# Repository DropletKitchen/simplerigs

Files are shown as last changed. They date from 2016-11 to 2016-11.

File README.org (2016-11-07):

* Simple Microfluidics Rigs with Inexpensive Board Cameras

*This page describes how to build an optics rig based on board cameras
for droplet microfluidics.*

This is a [[https://DropletKitchen.github.io][DropletKitchen]] project.

If not stated otherwise, the designs and documentation in this repository
is Copyright (c) 2016 Martin Fischlechner and DropletKitchen Contributors,
and made available under a
[[https://creativecommons.org/licenses/by/4.0/][Creative Commons Attribution 4.0 International (CC BY 4.0)]] License.

#+CAPTION: Image of the rig at several stages of the build. A] fully assembled rig. The inset shows the LED with inexpensive focusing optics. B] image of the openSCAD model used to design the first version. Use this model as a starting point for your own designs. C] setup without the x,y,z-stage. The inset shows the board camera with the flipped objective removed. D] x,y,z-stage.
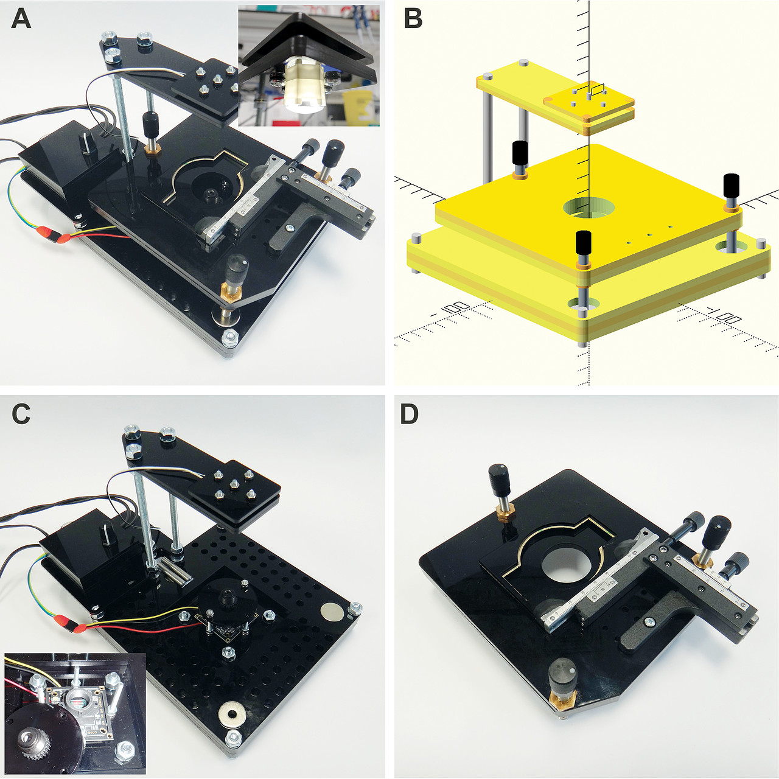
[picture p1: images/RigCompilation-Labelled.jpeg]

#+BEGIN_QUOTE
Image of the rig at several stages of the build. A] fully assembled
rig. The inset shows the LED with inexpensive focusing optics. B]
image of the openSCAD model used to design the first version. Use this
model as a starting point for your own designs. C] setup without the
x,y,z-stage. The inset shows the board camera with the flipped
objective removed. D] x,y,z-stage.
#+END_QUOTE

** Introduction
Many droplet microfluidic experiments have simple imaging
requirements, for example as a real-time quality control to ensure
droplet generation is running smoothly. This page shows how to build
simple microscopes with inexpensive board cameras. Flipping the
objective of the camera transforms the setup to a small
microscope. Magnification of the system is dependent on the distance
between the objective and the CCD or CMOS chip of the camera. In
contrast to scientific cameras, inexpensive consumer electronics
cameras or board cameras do not offer much control. They usually
self-regulate exposure times depending on the light available and
without frame rate adjustment, binning, or camera-triggering is
possible. BUT - they are incredibly cheap and often offer surprising
performance. Here we use a PS3 Eye camera and a CCD-camera that
outputs analog PAL video used for First Person View (FPV) drone
flying. While the PS3 eye is a rolling shutter camera, the board CCD
camera is global shutter, which is well suited for imaging fast
events.

#+CAPTION: This image compilation shows the performance of both cameras for observing a simple microfluidic droplet generator. The PS3Eye camera shows distortion effects due to its rolling shutter, but still allows to estimate droplet monodispersity (by virtue of width) up to velocities of 400 mm/s. The Sony CCD global shutter board camera lacks distortions, and yields useful images at higher velocities. With global shutter cameras the lightsource can additionally be strobed to enhance image quality. Due to the different chip sensor-objective distances of the setups used (see image below), the images of the PS3Eye have higher magnification. In its 'fast mode', the PS3Eye has a resolution of 320x240 (up to 180 fps) and is connected via USB. The Emax Sony 811 outputs analog video (PAL, 25fps) with a resolution of 976x582 pixels. Video can be displayed directly on a monitor. To use the camera with a computer, a framegrabber is needed.
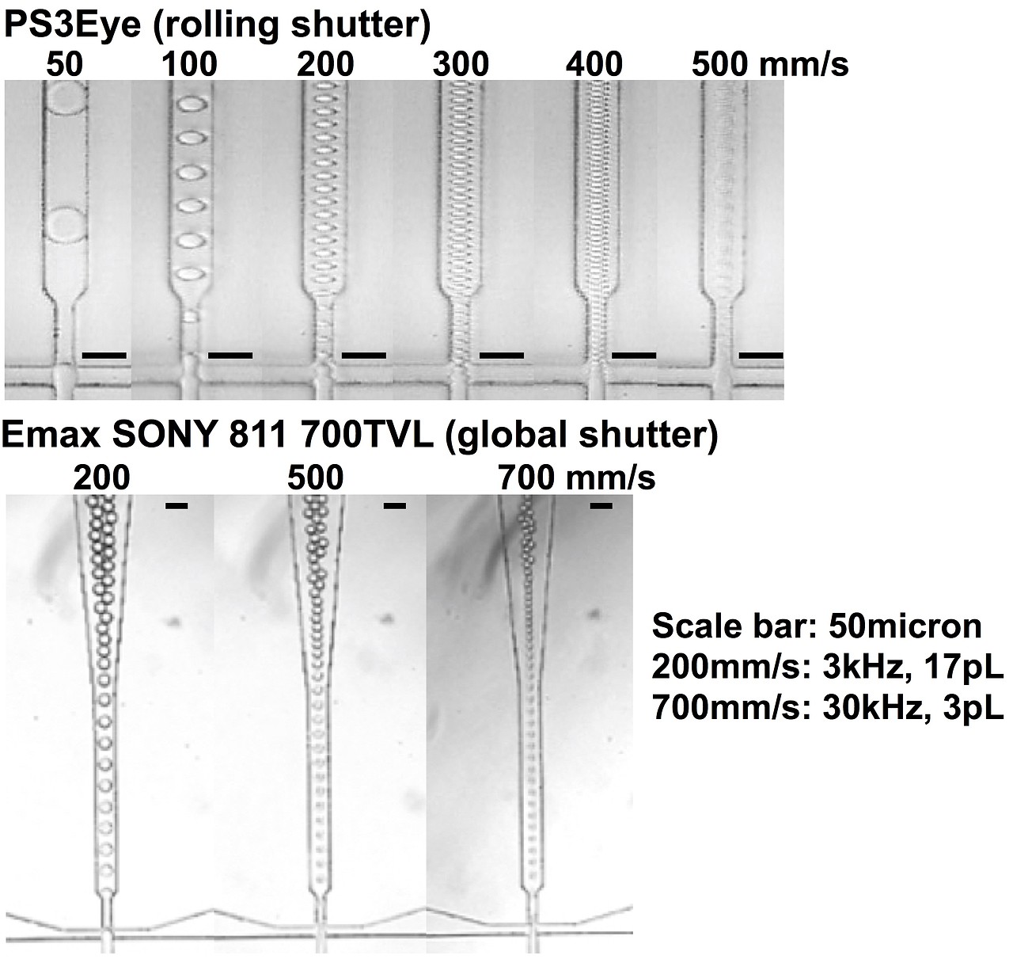
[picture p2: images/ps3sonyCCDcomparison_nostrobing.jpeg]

#+BEGIN_QUOTE
This image compilation shows the performance of both cameras for
observing a simple microfluidic droplet generator. The PS3Eye camera
shows distortion effects due to its rolling shutter, but still allows
to estimate droplet monodispersity (by virtue of width) up to
velocities of 400 mm/s. The Sony CCD global shutter board camera lacks
distortions, and yields useful images at higher velocities. With
global shutter cameras the lightsource can additionally be strobed to
enhance image quality. Due to the different chip sensor-objective
distances of the setups used (see image below), the images of the
PS3Eye have higher magnification. In its 'fast mode', the PS3Eye has a
resolution of 320x240 (up to 180 fps) and is connected via USB. The
Emax Sony 811 outputs analog video (PAL, 25fps) with a resolution of
976x582 pixels. Video can be displayed directly on a monitor. To use
the camera with a computer, a framegrabber is needed.
#+END_QUOTE

** Design
The model was first developed in openSCAD (http://www.openscad.org/)
and sliced for lasercutting
([[./files/RigSonyCCDPS3eyeBoardCameraOpenSCAD.scad]]). Later modifications
were done in a .dxf-file ([[./files/RigSonyCCDPS3eyeBoardCamera.dxf]]) with
Draftsight
(http://www.3ds.com/products-services/draftsight-cad-software/free-download/).
Starting with a 3D-model is helpful to play with overall dimensions
and shapes, but the design is quicker to modify in 2D-CAD at later
stages.

#+CAPTION: Parts for laser cutting.
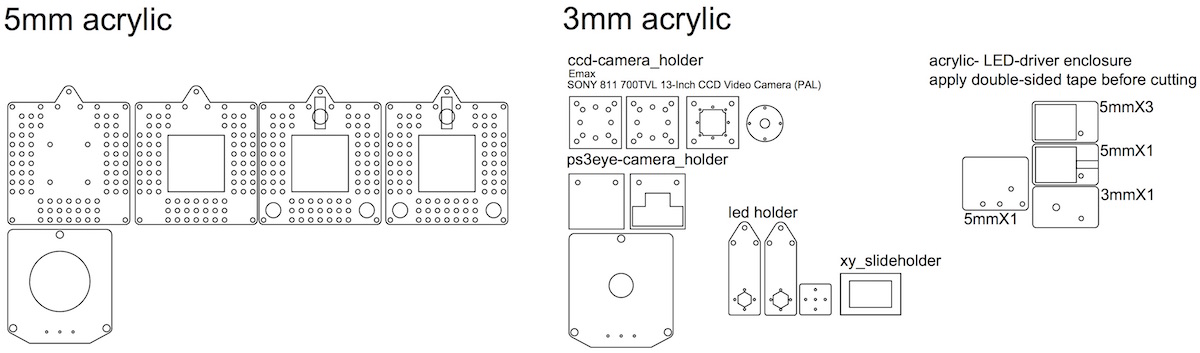
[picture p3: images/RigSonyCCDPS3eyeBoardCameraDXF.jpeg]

#+BEGIN_QUOTE
Parts for laser cutting.
#+END_QUOTE
** Materials

| Item                                                                   |      number | bought from                | part number    | approx cost (£) |
|------------------------------------------------------------------------+-------------+----------------------------+----------------+-----------------|
| Structural components                                                  |             |                            |                |                 |
|------------------------------------------------------------------------+-------------+----------------------------+----------------+-----------------|
| M6 Hex Screws (different lengths, eg l=16,20,25,30mm for flexibility)  |        many | RS or other hardware shop  |                |              NA |
| M6 Nuts, Washers, 'shake-proof washers'                                |        many | RS or other hardware shop  |                |              NA |
| M6 Threaded Rods                                                       | 3x (~150mm) | hardware shop              |                |              NA |
| M3 Screws, Nuts and Washers (different lengths)                        |        many | RS or other hardware shop  |                |              NA |
| 3mm Acrylic Sheet (410x280mm)                                          | 1 pack of 5 | www.techsoft.co.uk         | TAAC3-R3-5-COL |              18 |
| 5mm Acrylic Sheet (410x280mm)                                          | 1 pack of 5 | www.techsoft.co.uk         | TAAC3-R5-5-COL |              25 |
| Double-Sided Tape (3M, 468MP or 467MP), optional but nice to have      |           1 | RS                         | 842-1089       |              50 |
|------------------------------------------------------------------------+-------------+----------------------------+----------------+-----------------|
| XYZ-stage                                                              |             |                            |                |                 |
|------------------------------------------------------------------------+-------------+----------------------------+----------------+-----------------|
| Fine Adjustment Screw with Knob, 1/4"-80, 2.00" Long                   |           3 | Thorlabs                   | FAS200         |              17 |
| Locking Phosphor-Bronze Bushing with Nut, 1/4"-80, L=0.50"             |           3 | Thorlabs                   | N80L6P         |              21 |
| XY-stage from eBay (search 'microscope stage')                         |           1 | eBay                       |                |          max 20 |
| Eclipse 20mm Threaded Hole Neodymium Ring Magnet                       |           1 | RS                         | 792-4565       |               7 |
| Eclipse 20mm Neodymium Disc Magnet (3each, we use 5 for assembly)      |           2 | RS                         | 695-0184       |              22 |
| Short Steel Rods (magnetic) 20-40mm long, 5-6mm in diameter            |           2 | NA                         | NA             |              NA |
|------------------------------------------------------------------------+-------------+----------------------------+----------------+-----------------|
| Light                                                                  |             |                            |                |                 |
|------------------------------------------------------------------------+-------------+----------------------------+----------------+-----------------|
| RECOM POWER RCD-24-0.70/W/X3 LED Driver Adjustable                     |           1 | Farnell                    | 1793223        |              13 |
| OPULENT  REBEL-STAR-ES-NW200  High Brightness LED                      |           1 | Farnell                    | 2110405        |               4 |
| Polymer Optics 141/180, Lens Assembly                                  |           1 | RS                         | 665-6573       |               3 |
| Stripboard, 10kOhm Potentiometer                                       |             | eg Farnell, RS or other    |                |              NA |
| Male/Female 0.1" PCB Connectors                                        |             | eg Farnell, RS or other    |                |              NA |
| Sugru for isolation of wire connections...                             |           1 | cpc Farnell                | MK00041        |               6 |
| Epoxy Glue                                                             |          NA |                            | NA             |              NA |
|------------------------------------------------------------------------+-------------+----------------------------+----------------+-----------------|
| Optics/Cameras                                                         |             |                            |                |                 |
|------------------------------------------------------------------------+-------------+----------------------------+----------------+-----------------|
| Sony Playstation 3 Eye Camera (=rolling shutter)                       |           1 | amazon.co.uk               |                |              ~7 |
| Emax SONY 811 700TVL 1/3-Inch CCD Video Camera (=global shutter)       |           1 | www.unmannedtechshop.co.uk | CC7-E5A-55E    |              19 |
|------------------------------------------------------------------------+-------------+----------------------------+----------------+-----------------|

** Assembly
*** Optics
- disassemble the PS3 eye camera, you will have to remove some plastic
  on the objective (glued) to be able to flip it. The SonyCCD
  camera can be used as is, just remove the objective.

- attach the flipped objective to the camera in a way that no light
  can enter from the sides. This can either be done by clamping or
  glueing (see image below). If you want to improve magnification,
  enlarge the distance between camera-chip and objective by using a
  3D-printed tube or stack of acrylic rings. In this design
  adapter-plates were used that allow cameras to be easily exchanged. On the
  other hand they can also be just attached with some Sugru or hot
  melt glue.

#+CAPTION: Left: Playstation3 Eye camera with inverted optics. Magnification is controlled via the length of a 3D-printed tube. Right: Sony CCD board camera with inverted optics mounted with a sheet of acrylic.
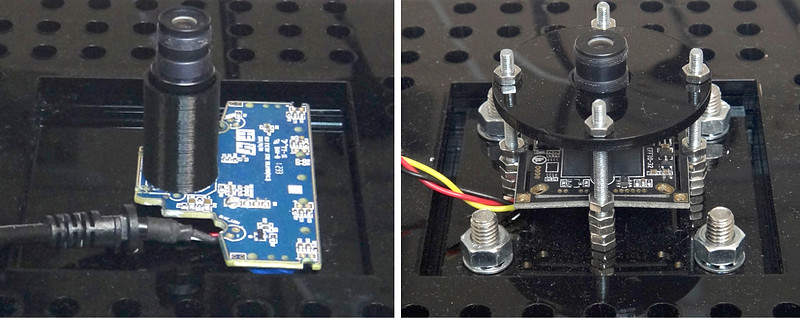
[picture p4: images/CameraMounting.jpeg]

#+BEGIN_QUOTE
Left: Playstation3 Eye camera with inverted optics. Magnification is
controlled via the length of a 3D-printed tube. Right: Sony CCD board
camera with inverted optics mounted with a sheet of acrylic.
#+END_QUOTE

*** Structure
Assembling the rig is straightforward; have a look at the image
above. Make sure that your components fit - if you change the design,
just measure components with a caliper and use exactly those
dimensions for holes etc. Laser cut parts usually results in a tight
fit. The camera with the inverted objective is held in place by
clamping it with acrylic sheets and M3 screws.

The stage is mounted on three optics screws with spherical ends in a
kinematic fashion - which defines the position of the stage by resting
on 6 points of contact. This is ideally 3 points on one, 2 on the
next, and one on the third. Here strong magnets are used to fix the
stage on its support - a ring magnet on the first side (a small cheat
but works well), 2 stacked disk magnets that magnetize two small steel
rods on top, and a stack of three disk magnets on the third point.
This assembly allows you not only to control z distance (focus), but
you can also tilt the stage and therefore have some movement in
x,y. For convenience, adding an inexpensive x,y stage is
recommended. They all differ a bit, so make sure you adapt the files
accordingly.

*** Light
For the lightsource, a star-shaped white high power LED is used which
is controlled by an adjustable LED driver. A M3 screw is used as a
heat sink and also holds the LED in place. The LED driver, a
potentiometer used to control brightness and an on/off switch is
soldered onto stripboard and then packaged in an acrylic enclosure. It
does not have to bear a lot of load, so the enclosure is based on cut
acrylic slides with double-sided tape added on one side before
cutting. This allows the structural components to be bonded together.
To focus the light of the LED onto the chip, inexpensive plastic
lenses are used. For assembly, just use a dab of epoxy glue. Do not
use 'Superglue', as cyanoacrylate vapours render optics components
cloudy over time.  Change the distance between LED and the stage such
that the image on the camera is overexposed when the LED is fully on
and the camera is set automatically to the smallest exposure time
possible. This allows you to get the best possible images of
fast-moving objects with your setup. Below is the circuit diagram for
wiring if you use the Recom LED-driver. If you want an on/off switch,
just wire it to the voltage or ground wire. Almost any power supply
will do (>=1A, 5-36V).

#+CAPTION: Circuit diagram for the Recom LED driver.
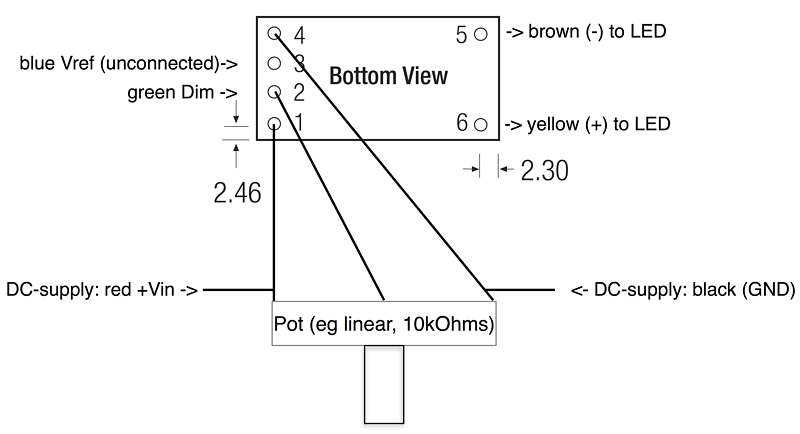
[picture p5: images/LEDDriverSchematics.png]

#+BEGIN_QUOTE
Circuit diagram for the Recom LED driver.
#+END_QUOTE

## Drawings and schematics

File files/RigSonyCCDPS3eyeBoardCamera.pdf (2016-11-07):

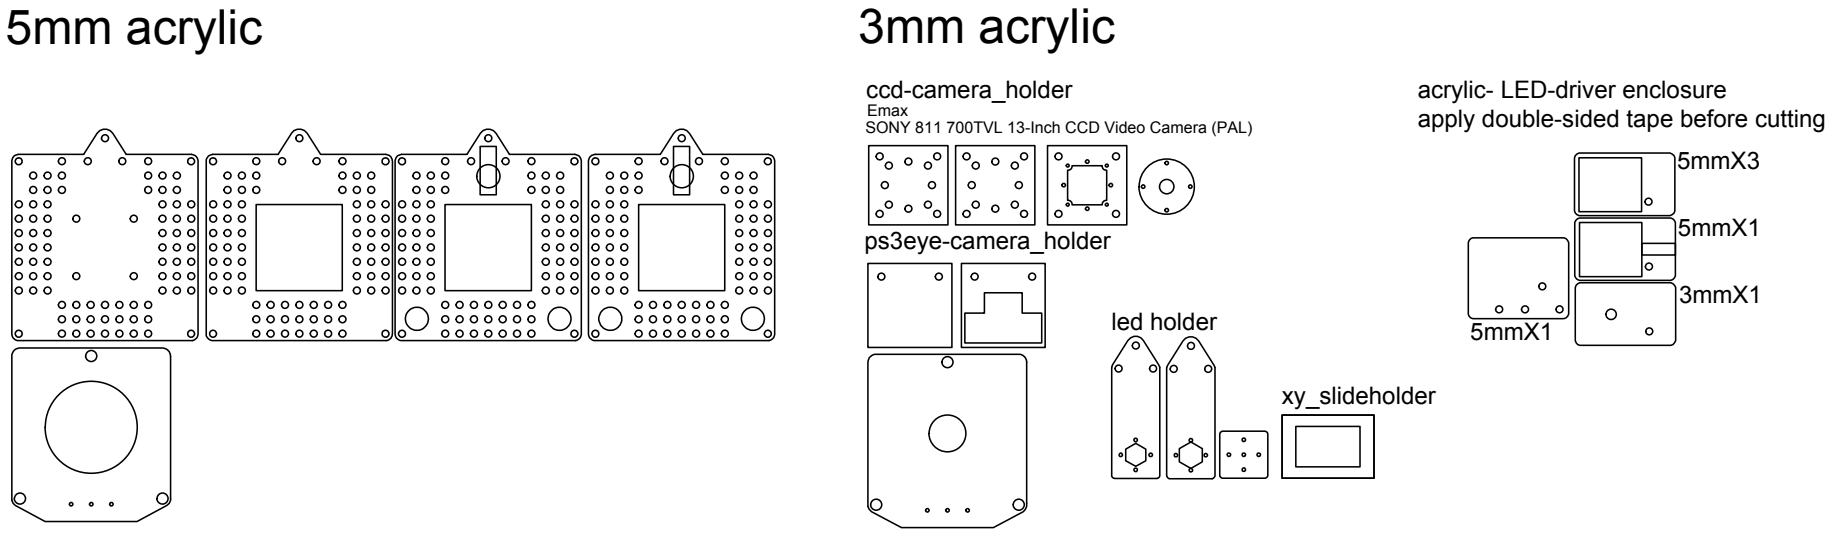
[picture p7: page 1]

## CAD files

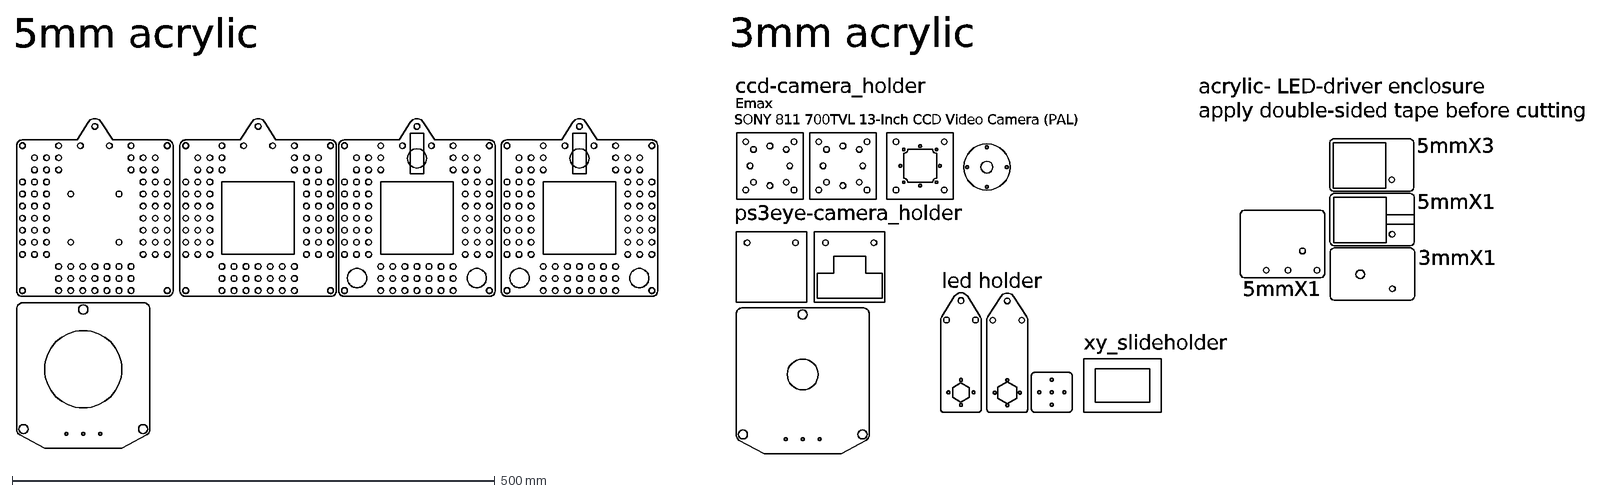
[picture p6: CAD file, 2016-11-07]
files/RigSonyCCDPS3eyeBoardCamera.dxf
led holder
xy_slideholder
ccd-camera_holder
Emax SONY 811 700TVL 13-Inch CCD Video Camera (PAL)
ps3eye-camera_holder
acrylic- LED-driver enclosure apply double-sided tape before cutting
3mm acrylic
5mm acrylic
5mmX3
5mmX1
3mmX1

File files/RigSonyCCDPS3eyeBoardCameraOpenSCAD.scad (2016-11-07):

/////////////////////////////
//////Simple rig/////////////
/////////////////////////////


//the parts have been sliced into sheets (for lasercutting), if you 3D print, make 'combined' .stl-files of sheet1&2 (bottom part), sheet3&4 (stage), sheet5&6 (LED holder), and sheet7 (to clamp down the LED), by compiling, rendering and exporting the parts together 

//optional parts are commented out (remove '*' to see)
// add '#' to highlight part/subtraction in red (useful to find and investigate parts) 

////////////////////////////////////////////////////
//VARIABLES - change them according to your needs //
////////////////////////////////////////////////////

roundness_dia = 6;//bottom part: radius of rounded edges (should be bigger than radius screws: M6>3)
roundness_dia2 = 7;//xyz-stage, take care for it being big enough for leadscrews and wall
roundness_dia3 = 3;//roundness of lightfixtures
//
x=75;//x-dimension of screwholes (stands) of bottom plate in mm; min size required for fitting our x/y stage in is around x= 70mm
z=5; //sheet thickness if you use a laser cutter
zLED=3; //sheet thickness LED and lens fixture, again, for lasercutting
min_wallsize = 0;//distance between cut holes and part outlines, use >=3 when using M6 screws to accomodate the nuts, only used in lightfixtures, quite obsolete right now
prop=5;//proportion x:light fixture holes

//variables for kinematic stage
radius_centerhole1 = 16; // r of centerhole_stage, bottom plate
radius_centerhole2 = 16; // r of centerhole_stage, top plate

radius_screws = 3; //radius of screws used (default M6)
radius_leadscrewnut = 4.8; //radius of leadscrew-nut for z-stage


diameter_steelbar = 6; // diameter for steelbar-inserts, kinematic stage
radius_magnet = 10; //radius of magnets used for kinematic stage

y=(x-radius_screws-radius_magnet);//dimension (leadscrew-holes) of stage

stage_height = 30; //height of stage (just for drawing)
light_height = 100; //height of light fixture (just for drawing)
screw_connector1_height = 85; //height of screw connector1 (just for drawing), optional part (commented out)
screw_connector2_height = 70; //height of screw connector2 (just for drawing), optional part (commented out)

//Light fixture variables
LED_radius = 11.5; //half of the LED diameter
makesmaller = 1.5; //hole for LED to sit on (must be smaller than LED diameter)
LED_radius1 = LED_radius - makesmaller;
radius_LEDscrews = 1.5; //radius of screws on LED part (defaultM3)

//lens fixture variables (optional parts if you want to use a standard optics lens to focus the light onto the sample, commented out)
radius_LENS = 6.5; //radius of collimating lens used (1/2-inch optics)
indent_LENS = 1; //make radius smaller for parts that hold lens in place

//space to mount PS3 eye camera (so that the assembly doesn't have to be that high
ps3_space = 75;


//optional mounted xy-stage: variables
xystagemiddleholedistance = 55;//check your stage and figure out where/how to mount
xystagemiddleholeradius = 1.75;
xystageoffcenterholedistance = 55;
xystageoffcenterholeoffset = 17.5;
xystageoffcenterholeradius = 1.5;

//variables for illustration of added hardware
radius_leadscrew = 3.14;


/////////////////////////////////////////////////////////////
/////////////////SHEET1 (bottom part)///////////////////////
////////////////////////////////////////////////////////////

difference ()
{

$fn=50;
   color ("yellow", a=1.0)
   translate ([0,0,0])
   hull()
   {
        translate ([x,x,0])
        cylinder(r = roundness_dia, h = z, $fa=1, $fs=0.5, center = true);
        translate ([-x,x,0])
        cylinder(r = roundness_dia, h = z, $fa=1, $fs=0.5, center = true);
        translate ([x,-x,0])
        cylinder(r = roundness_dia, h = z, $fa=1, $fs=0.5, center = true);
        translate ([-x,-x,0])
        cylinder(r = roundness_dia, h = z, $fa=1, $fs=0.5, center = true);
   }


//screwholes
//top right
translate ([x, x, -z]) 
cylinder(r = radius_screws, h = 2*z, $fa=1, $fs=0.5);
//top left
translate ([-x, x, -z]) 
cylinder(r = radius_screws, h = 2*z, $fa=1, $fs=0.5);
//bottom right
translate ([x, -x, -z]) 
cylinder(r = radius_screws, h = 2*z, $fa=1, $fs=0.5);
//bottom left
translate ([-x, -x, -z]) 
cylinder(r = radius_screws, h = 2*z, $fa=1, $fs=0.5);

//screwholes for light-fixture
//top right
translate ([x/prop, x, -z]) 
cylinder(r = radius_screws, h = 2*z, $fa=1, $fs=0.5);
//top left
translate ([-x/prop, x, -z]) 
cylinder(r = radius_screws, h = 2*z, $fa=1, $fs=0.5);
}

/////////////////////////////////////////////////////////////////////
////SHEET2 (bottom part, second layer with steel bars)//////////////
////////////////////////////////////////////////////////////////////
translate ([0,0,z]) 
{
difference ()
{

$fn=50;
   color ("gold", a=1.0)
   translate ([0,0,0])
   hull()
   {
        translate ([x,x,0])
        cylinder(r = roundness_dia, h = z, $fa=1, $fs=0.5, center = true);
        translate ([-x,x,0])
        cylinder(r = roundness_dia, h = z, $fa=1, $fs=0.5, center = true);
        translate ([x,-x,0])
        cylinder(r = roundness_dia, h = z, $fa=1, $fs=0.5, center = true);
        translate ([-x,-x,0])
        cylinder(r = roundness_dia, h = z, $fa=1, $fs=0.5, center = true);
   }
//centerhole
translate ([0, 0, 0]) 
cube([ps3_space,ps3_space,3*z],center=true);
//screwholes
//top right
translate ([x, x, 0]) 
cylinder(r = radius_screws, h = 2*z, $fa=1, $fs=0.5);
//top left
translate ([-x, x, 0]) 
cylinder(r = radius_screws, h = 2*z, $fa=1, $fs=0.5);
//bottom right
translate ([x, -x, 0]) 
cylinder(r = radius_screws, h = 2*z, $fa=1, $fs=0.5);
//bottom left
translate ([-x, -x, 0]) 
cylinder(r = radius_screws, h = 2*z, $fa=1, $fs=0.5);

//screwholes for light-fixture
//top right
translate ([x/prop, x, 0]) 
cylinder(r = radius_screws, h = 2*z, $fa=1, $fs=0.5);
//top left
translate ([-x/prop, x, 0]) 
cylinder(r = radius_screws, h = 2*z, $fa=1, $fs=0.5);

//magnet-inserts
//bottom right
translate ([y, -y, 0]) 
rotate([0, 0, 90])
cylinder(h = 2*z, r=radius_magnet, $fa=1, $fs=0.5,center = true);

//bottom left
translate ([-y, -y, 0]) 
rotate([0, 0, -90])
cylinder(h = 2*z, r=radius_magnet, $fa=1, $fs=0.5,center = true);

//top middle
translate ([0, y, 0]) 
rotate([0, 0, 45])
cylinder(h = 2*z, r=radius_magnet, $fa=1, $fs=0.5,center = true);
//top middle (steelbar-insert)
translate ([0, y, 0]) 
rotate([0, 0, 90])
cube ([2*radius_magnet+diameter_steelbar, 2*diameter_steelbar,2*z], center = true);


}}

/////////////////////////////////////////////////////////////////////
////SHEET2.5 (bottom part, second layer with steel bars)//////////////
////////////////////////////////////////////////////////////////////
translate ([0,0,2*z]) 
{
difference ()
{

$fn=50;
   color ("yellow", a=1.0)
   translate ([0,0,0])
   hull()
   {
        translate ([x,x,0])
        cylinder(r = roundness_dia, h = z, $fa=1, $fs=0.5, center = true);
        translate ([-x,x,0])
        cylinder(r = roundness_dia, h = z, $fa=1, $fs=0.5, center = true);
        translate ([x,-x,0])
        cylinder(r = roundness_dia, h = z, $fa=1, $fs=0.5, center = true);
        translate ([-x,-x,0])
        cylinder(r = roundness_dia, h = z, $fa=1, $fs=0.5, center = true);
   }
//centerhole
translate ([0, 0, 0]) 
cube([ps3_space,ps3_space,3*z],center=true);
//screwholes
//top right
translate ([x, x, 0]) 
cylinder(r = radius_screws, h = 2*z, $fa=1, $fs=0.5);
//top left
translate ([-x, x, 0]) 
cylinder(r = radius_screws, h = 2*z, $fa=1, $fs=0.5);
//bottom right
translate ([x, -x, 0]) 
cylinder(r = radius_screws, h = 2*z, $fa=1, $fs=0.5);
//bottom left
translate ([-x, -x, 0]) 
cylinder(r = radius_screws, h = 2*z, $fa=1, $fs=0.5);

//screwholes for light-fixture
//top right
translate ([x/prop, x, 0]) 
cylinder(r = radius_screws, h = 2*z, $fa=1, $fs=0.5);
//top left
translate ([-x/prop, x, 0]) 
cylinder(r = radius_screws, h = 2*z, $fa=1, $fs=0.5);

//magnet-inserts
//bottom right
translate ([y, -y, 0]) 
rotate([0, 0, 90])
cylinder(h = 2*z, r=radius_magnet, $fa=1, $fs=0.5,center = true);

//bottom left
translate ([-y, -y, 0]) 
rotate([0, 0, -90])
cylinder(h = 2*z, r=radius_magnet, $fa=1, $fs=0.5,center = true);

//top middle
translate ([0, y, 0]) 
rotate([0, 0, 45])
cylinder(h = 2*z, r=radius_magnet, $fa=1, $fs=0.5,center = true);
//top middle (steelbar-insert)
translate ([0, y, 0]) 
rotate([0, 0, 90])
cube ([2*radius_magnet+diameter_steelbar, 2*diameter_steelbar,2*z], center = true);


}}


/////////////////////////////////////////////////////////////
/////////////////SHEET3 (xyz-stage, first layer)//////////////////////
////////////////////////////////////////////////////////////

difference ()
{
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
